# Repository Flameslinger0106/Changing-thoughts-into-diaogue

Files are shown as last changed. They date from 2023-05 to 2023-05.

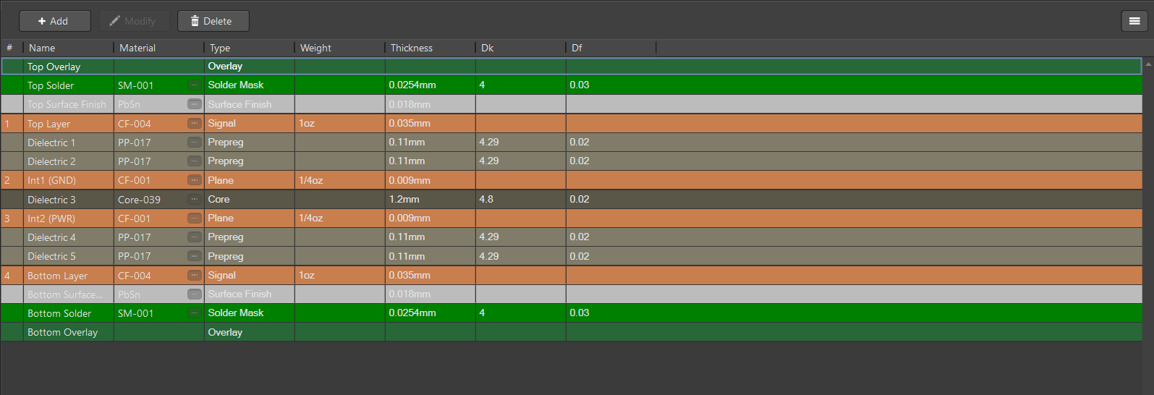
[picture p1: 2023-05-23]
Layer stack manager.PNG

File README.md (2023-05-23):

# Changing-thoughts-into-diaogue
This repository contains the Altium PCB design for a project that we had in which we had to convert thoughts into audible dialogue.

There is a report attached alongside the actual files associated with the design that contains all the restrictions that were to be taken into account while designing the said PCB.

If you are having difficulty in understanding the motive or working please look at the "Report file for T-A project" in the file section.

Please do not copy and paste the files as they are and make sure to email me first at - anmolyadav0106@gmail.com if you need to talk about importing certain parts of the project.

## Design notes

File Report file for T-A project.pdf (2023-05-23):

Mohammed Arib z5208042

Ashish Dutta

Jack Walsh

Anmol Yadav

# ELEC4123 ELECTIVE TASK REPORT

TABLE OF CONTENTS

PROBLEM STATEMENT

The overarching design problem was collectively perceived by the team to be: “Electronically translating a patient’s thoughts into accurate and audible dialogue.”

IMPORTANT FEATURES

- Must think about the practicality of the design approach. Is it viable to use in real life? How is it powered? How does it interact with the patient?
- Interfacing between tasks.

FILTRATION

Upon initial research and inspection of the signals provided, it was discovered that EEG signals occupy microvolt level amplitudes. Also, these signals are highly susceptible to noise (such as muscle movements, eye saccades and pink noise).

Key challenges are:

- To amplify the EEG signals to MCU voltage range with low distortion and noise.
- To find a balance with the trade-off between the noise reduction circuitry and minimising component noise. More components means more noise reduction functionality but more components also means more component noise.

SIGNAL PROCESSING

The goal is to achieve a high detection rate in real time. The best algorithms that give good detection rates have higher time complexities, hence they are harder to implement in real time.

Key challenges are:

- Balance the trade-off between real time processing speed and effective detection rate.
- Navigating ambiguities in breaking down a large signal into smaller words to mimic regular human speech, i.e., what is a reasonable ‘frame’ size?

AUDIO PRODUCTION

Key Challenges are:

- Taking a low voltage analogue signal and amplifying it whilst maintaining a delicate balance between efficiency and THD/spectral characteristics.
- Keeping efficiency high while minimising power consumption which would require a balance between complexity and component count.
- Modelling and accounting for the non-idealities of a realistic speaker.

CONSOLIDATION

It is important to consider how all the tasks will come together to work as one holistic system to ensure outputs remain precise and it is safe to use in a medical environment.

Key Challenges are:

- Condensing all tasks onto a PCB of minimal size so it is practical for real life use
- Minimising signal interference (such as cross talk, ground loops, parasitic capacitance, EMI) for accurate functionality.

BEHAVIOURAL CHALLENGE

- The large breadth of knowledge required to breakdown and complete the task and the difficulty in distributing tasks among the team based on individual expertise and availability

DESIGN CONCEPT AND REASONING

OBJECTIVES & BENCHMARKS-

FILTRATION

The main objective for the filtration part of the circuit is to aim for a balance between noise reduction circuitry and minimizing component noise.

For this part, it is ideal to implement a gain amplifier to make it easier for the microcontroller to sort the input signals into its corresponding bands.

Benchmarks to achieve:

- Realistic noise figure for the filtration part of the circuit is around 2dB-15dB
- ADC selection with high GBP and High slew rate
- Low input referred noise of around 1nV/√Hz
- 3dB cut off at 40Hz for matching the signal bands

SIGNAL PROCESSING

Key objective is to detect the input signals in real time for outputting through a speaker.

Benchmarks to achieve:

- Sampling and Time resolution: Bounded by the Nyquist criterion to avoid aliasing. Sampling rate of at least 256Hz must be chosen.
- Feature extraction scheme: Timing must be real time i.e., processing time on the order of 300ms - comparable to buffer size.
- Detection rate: Must accomplish at least 95% for a usable experience.
- Buffering: Simulate real time audio pause. 300ms pause
- Noise performance: Must still achieve >= 95% detection rate in non-ideal conditions.

AUDIO PRODUCTION

Objective for this part includes creating a Power supply for the first two parts of the circuit as well as making sure the output is relayed through the speaker.

Benchmarks to achieve:

- Bandwidth and flatness: Bandwidth roughly 20k because of limits for human hearing bandwidth 3db drop off should be between low: 20hz, high: 20khz
- Open loop bandwidth: required to be high
- Power delivered: Low as reasonably possible, limit on active biasing etc. Balance with efficiency - 40mW
- THD: the main focus, below 1% and ideally 0.1%. Achieved through a closed loop system that linearizes the output over the crossover distortion period (refer to Deliverable 4)
- AB amplifier choice
- Limit the component count. Zobel network tuning to particular TSP

SOLUTION & REASONING

OVERVIEW OF SOLUTION CONCEPT

Low-noise preamplifier | Microcontroller (feature extraction)

Power amplifier speaker output

FILTRATION

Challenge 1:

To amplify the EEG signals to MCU voltage range with low distortion and noise.

Noise filtration is achieved with a low noise amplifier, low pass filtering and active removal of noise sources. EEG input voltage range is 10-100uV, output range is 0-3.3V.

Key methods to overcome this challenge were:

- Putting op amps in parallel to improve spectral noise characteristics
- Choosing low noise amplifiers
- Performing second order low pass filtering
- Using adjustable gain amplifier to

Meeting objectives:

Through a component choice of low noise precision op amps, an average noise figure of 3.57db was achieved. Furthermore, small resistor values were used to keep component noise low.

Challenge 2:

To find a balance with the trade-off between the noise reduction circuitry and minimizing component noise.

This challenge was met by experimenting with different op amp configurations. Initially only one op amp was used for the preamplification, however, noise at the output was relatively high. Parallelising op amps reduced noise spectral density overall however increased space on the PCB. The optimal number of op amps used to solve this problem were 6. Any less and the output had more noise and any more than 6, and component noise and space increases didn’t justify the use.

To simulate component noise, a variety of noise sources were added simulating the effect of an additional component.

Meeting objectives:

Noise was significantly attenuated using low pass filters hence high frequency noise above 40hz was reduced significantly.

SIGNAL PROCESSING

Challenge 1:

Balance the trade-off between real time processing speed and effective detection rate.

In order to meet this challenge effectively, a hybrid implementation of short-time Fourier transform (high speed, lower complexity, mediocre detection rate) and peak detection for detecting false positives for beta band (higher complexity, slower speed). Hence by utilizing this approach a balance was achieved between approach complexity and computational complexity.

Meeting objectives:

Upon implementation of these methods a detection rate of 96% was recorded across all samples and custom test cases. Furthermore, this approach allowed real time processing.

Challenge 2:

Navigating ambiguities in breaking down a large signal into smaller words to mimic regular human speech, i.e., what is a reasonable ‘frame’ size

For the solution concept to meet this challenge, a literature review was conducted for obtaining lengths of pauses in natural speech. Similarly, the frame size (after research) was chosen to be 1sec to mimic the patterns of user thought. The output between words was buffered using a 0 padded signal with an average buffer size of 0.3seconds, and the processing speed was fast enough to process the next frame whilst buffering was occurring -offering a seamless experience.

Meeting objectives:

Here the frame size, buffer length and sampling rate choices allowed the solution concept to effectively break apart the signal and deliver a user experience worthy of usage.

AUDIO PRODUCTION

Novel features: Adjustable volume control, component minimisation, Zobel network, extremely high bandwidth, outstanding THD, minimizing cross-over distortion

Challenge 1:

Taking a low voltage analogue signal and amplifying it whilst maintaining a delicate balance between efficiency and THD/spectral characteristics.

To meet this challenge a choice was made between class A, B and AB amplifiers. Class A amplifiers have low efficiency and low distortion, AB amplifiers have better efficiency and slightly higher distortion, and class B amplifiers have the highest efficiency and highest distortion.[1] Minimizing THD was the key priority, as THD related to the clarity of produced sounds. Efficiency was the next important metric. To strike a balance between the two, a class AB amplifier configuration was used.

Meeting objectives:

Using this method, a THD of 0.1%, higher efficiency approaching 50% was reported. The solution concept minimized power draw to 40mW by minimizing the number of active components in the design.

Challenge 2:

Modelling and accounting for the non-idealities of a realistic speaker.

The mass of a speaker, inductance, capacitance, force of membrane vibration and other key real-world phenomena require extra attention in order to reproduce a realistic model for audible sound. A Zobel network was implemented to tune these electromechanical parameters also known as Thiele/Small Parameters (TSP).[2] This network serves as a practical method to neutralize instabilities at high frequencies, coil inductance and other realistic non idealities.

Meeting objectives:

The implementation of this section culminated in effective gain and bandwidth (2.51 and 1.061Mhz respectively).

HIGH LEVEL BLOCK DIAGRAM

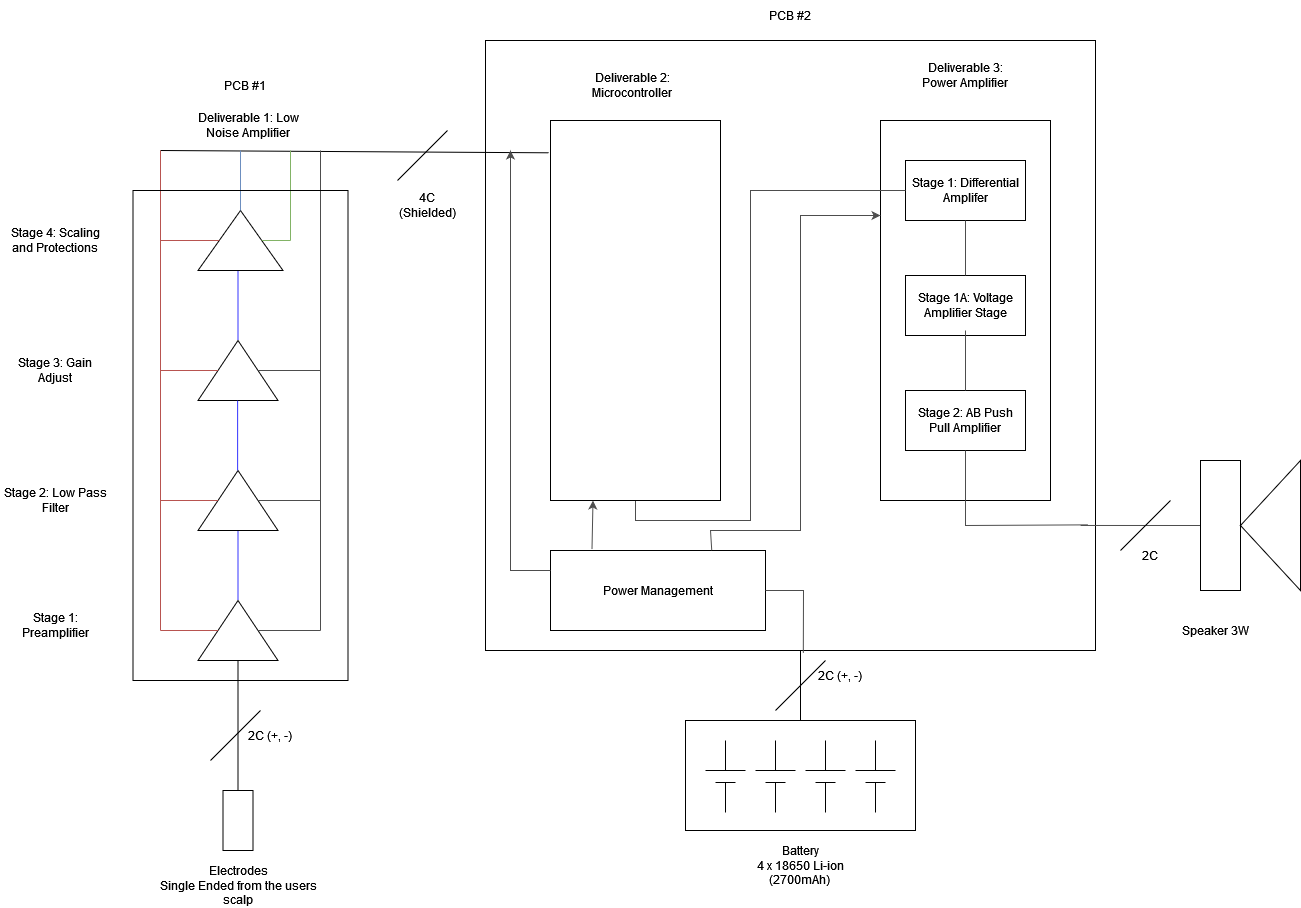
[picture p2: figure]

Figure 1 High level block diagram

TASK ALLOCATION

The tasks were allocated based on each member’s strength and ultimately what they felt the most comfortable with to maximize productivity and reduce any delays caused by lack of fundamental knowledge for their allocated task.

Although each deliverable was primarily handled by one individual, other team members would be often encouraged to pitch in with any suggestions or ideas relevant to the task at hand.

Primarily, task and time allocation for each deliverable and its subcomponent contributors was done through a Gantt chart as shown below. It can be inferred from the Gantt chart how each deliverable was primarily handled individually by each of the group members.

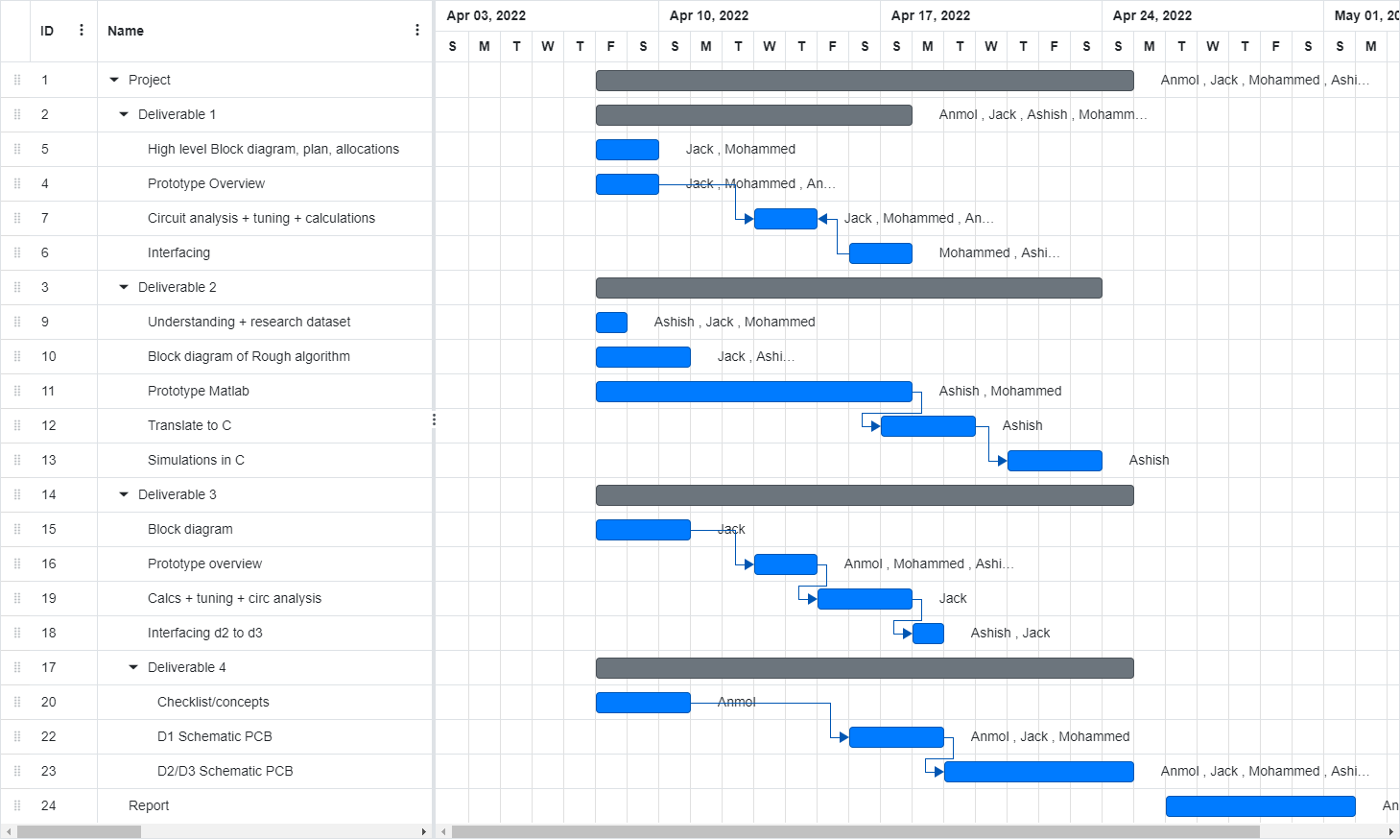
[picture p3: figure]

Figure 2 Gantt Chart

TASK DESCRIPTIONS

DELIVERABLE 1

Author: Mohammed Arib

1.1 INTRODUCTION

EEG signals contain a high amount of random and/or repetitive noise which hinders effective analysis of useful information hidden within the signal. This recording circuit is purposed to extract this information by removing redundant noise artifacts through effective filtration techniques while also amplifying the signal so it can be processed on the MCU.

1.2 NOVEL FEATURES

- Parallel pre-amplifier configuration for better noise performance [3]
- Adjustable gain amplifier to record wider variety of signals such as EMG and LFP
- Removing large noise artefacts such as blinking, unstable electrode contacts, swallowing [4]
- Effective bipolar to unipolar signal conversion to minimise component count
- Minimising PCB size by using an even number of op amps to utilise dual package ICs

1.3 STAGE 1: PRE-AMPLIFIER AND DC BLOCKER

Prior to designing the circuit, it was important to determine whether it is better to amplify before filtering or vice versa. Research shows that filtration should be conducted after low noise amplification to achieve the best possible noise figure [3], this is because filtering attenuates the signal bringing the voltage level close to the noise which would then be amplified giving a poor signal to noise ratio.

The first stage of the circuit is a pre-amplifier which allows the amplification of low voltages with low distortion. This was achieved by using a very low noise amplifier (LT1028) with a voltage noise density of 1nV/√Hz at 100Hz. The total noise density of the amplifier stage was significantly improved by implementing a parallel configuration of pre-amplifiers. For a two-level pre-amplifier configuration, the total input referred noise density is reduced by a factor of √2 [5]. This can be shown for a general number of op amps in parallel with the formula:

Total noise of op-amps = N/√n Where N is the noise density of the op-amp, n is the number of op-amps in parallel

Using the above formula for this circuit, the total input referred noise from the op-amps would be:

1/√2 = 0.7nV/√Hz

The total noise of this stage is further improved by choosing small feedback resistors to keep the impedance level and component voltage noise as low as possible.

The second part of this stage is a DC blocker which is used to remove any offset voltage present in the EEG signal. The blocker uses a simple topology of consisting an inverting op-amp followed by a decoupling capacitor at the output to remove the DC offset. It is necessary to remove any offsets in sounds signals to avoid static and crackling noises [6]. The effectiveness of the blocker can be visualised in Figure 2 and 3 showing the original EEG signal and the signal after offset removal.

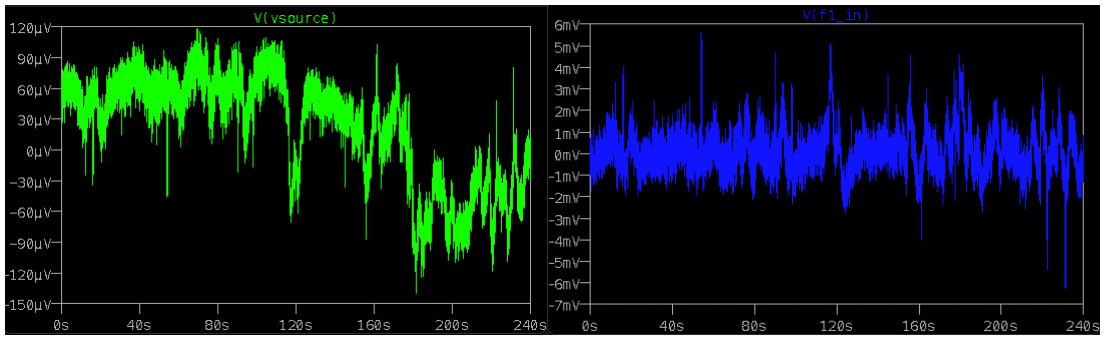
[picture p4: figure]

Figure 3 Original EEG signal with 60uV offset | Figure 4 EEG signal after DC blocker with no offset

1.4 STAGE 2: FILTRATION

The next stage of the circuit is a second order Low pass filter tuned to have a 3dB cut off at 40Hz (shown in Figure 4) to match the range of EEG signal bands from delta to beta. A higher order filter has higher attenuation for frequencies above the bandwidth therefore this stage uses a second order filter for a 40dB/dec drop after 40hz which can be seen in Figure 3.

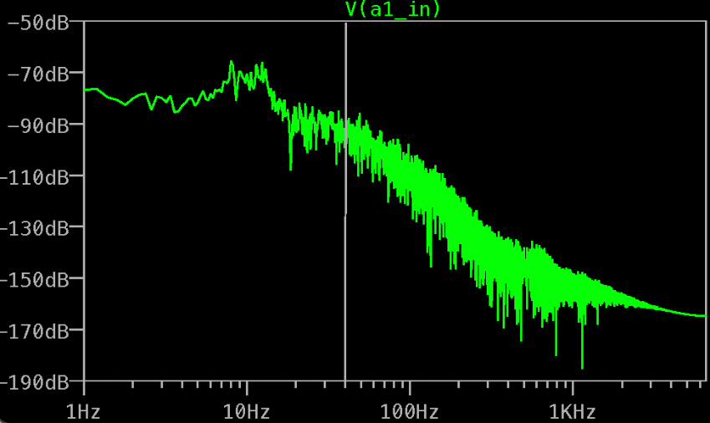
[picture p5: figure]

Figure 5 FFT of EEG signal with 40Hz point marked at grey line

A Sallen Key filter topology is used to construct the low pass filter due to its simple design and the ease of cascading RC components to achieve a higher order filter [7], hence reducing component count. This topology also minimizes the gain-bandwidth requirement of the op-amp so the same op-amp can be used as in the Stage 1 to keep a low voltage density and enable the use of the dual package IC available hence minimizing the PCB area and making the device more practical.

1.5 STAGE 3: ADJUSTABLE GAIN AMPLIFIER

The next stage is used to amplify the EEG signal while maintaining its spectral characteristics to increase the resolution up to the ADC voltage level. This is essential to do so that the signal can be accurately quantised and analysed in the MCU. To achieve this an adjustable gain amplifier is implanted using a simple inverting amplifier with a potentiometer as the feedback resistor.

Literature review states that EMG signals are used to record skeletal muscle activity with an amplitude range of 10-20mV [8] putting them at a much higher voltage level than EEG signals. The potentiometer allows the user to change the feedback resistance, in turn changing the gain of the amplifier to accommodate for signals with a greater voltage level.

Due to the high gain required to bring the signal to ADC voltage level of 3V as shown in Figure 5 and 6, the amplifier, LT1630, was chosen based on its high GBP (30Mhz) and slew rate (30V/us) characteristics. This amplifier also maintains it performance at a low supply of 3V which makes it suitable to use for battery powered systems such as this.

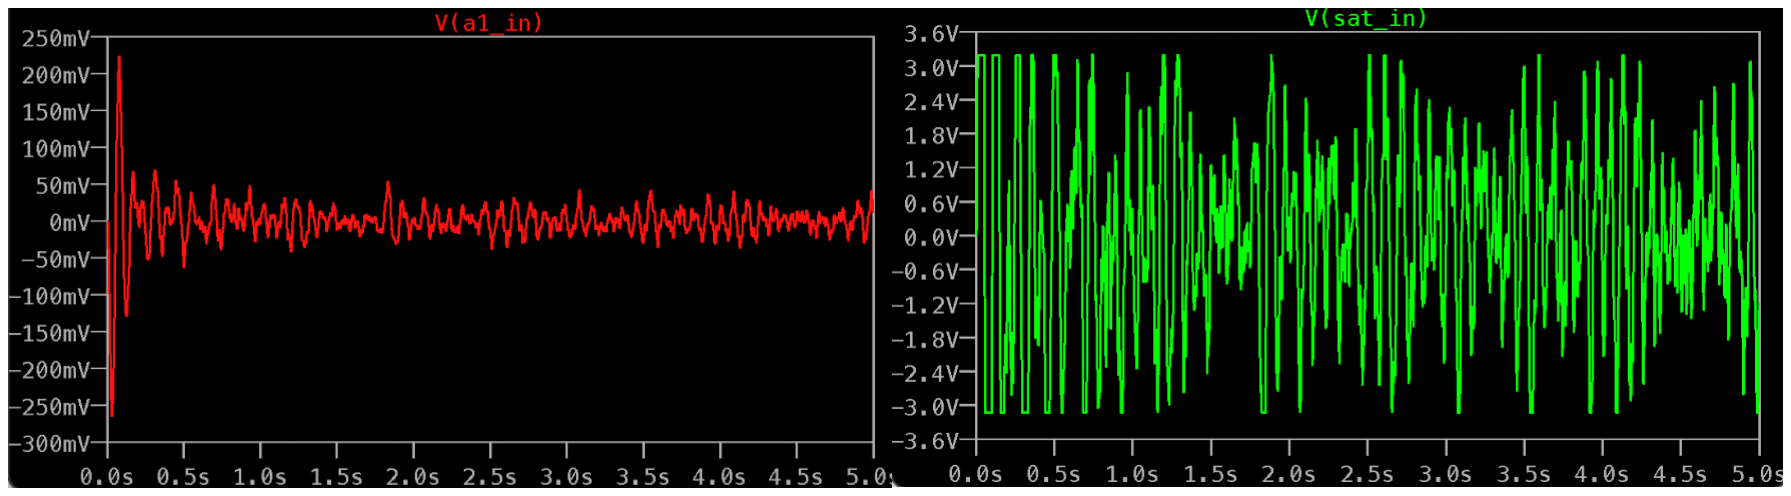
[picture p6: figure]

Figure 6 EEG Signal after LPF | Figure 7 Signal after amplification

1.6 INTERFACING AND ADC SELECTION:

Before explaining the final stage of the circuit, it is important to delve into how this circuit will be interfaced with the MCU and the choices need to be made to achieve that. The analogue signal that this circuits outputs needs to be passed into an ADC before it can be analysed in the MCU. When digitising an analogue signal, parameters such as noise floor and quantisation noise need to be considered.

Noise floor is the sum of the noise each individual component generates in the system [9]. The component noises are accounted for when calculating a noise figure for the system since noise and signal are independently extracted for input and output through LTspice when calculating the noise factor. An ideal noise figure is 0 and through research a realistic noise figure is said to be between 2dB-15dB [10]. The noise figure obtained for this circuit can be seen in the Figure 7 with the peak at approximately 10dB and an average of 3.57dB. Since EEG signals are very susceptible to noise a figure of 3.57dB is acceptable.

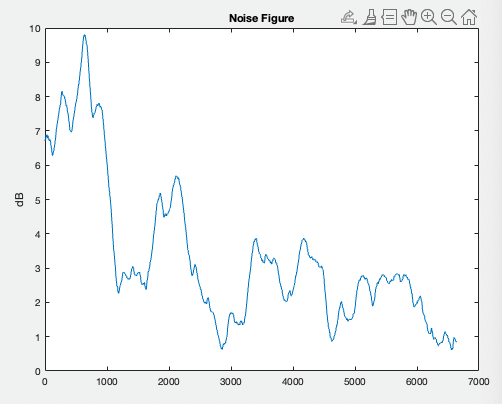
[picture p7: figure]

Figure 8 Noise Figure

Quantisation noise is an inevitable effect of converting an analogue signal to a discrete form. It is caused by rounding errors between the real analogue signal and the bit resolution of the ADC [11]. To reduce the quantisation noise level a low pass filter can be used at the output of the ADC which can be implemented digitally on the MCU.

Taking these parameters into consideration, the ADC built into the MCU will be sufficient for interfacing which would also reduce component count and minimise PCB size. The on-board ADC operates within a voltage range of 0-3.3V and has a sufficient resolution of 12 bits giving a dynamic range of 72.4dB for the system. This will appropriately map the analogue signal into the digital domain.

1.7 STAGE 4: SCALING AND PROTECTION

The final stage of this circuit is a unit gain buffer to convert the bipolar signal to a unipolar signal range which the ADC takes. A comparison between the two signals is shown in Figure 8 below, where the green signal is the output of the adjustable gain amplifier, and the blue signal is the output of the unity buffer.

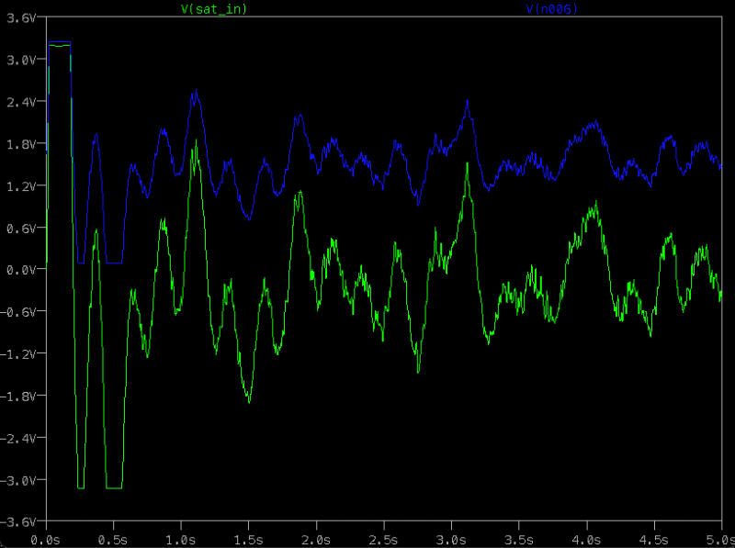
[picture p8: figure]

Figure 9 Output of amplifier vs output of buffer

The op-amp used for this stage does not require any new or unique characteristics compared to the previous stage therefore the same op-amp is used. Also, selecting the same op-amp allows for the use of the dual package IC hence making the device more practical by decreasing the size of the PCB.

The second purpose of this stage is to saturate the signal, so it does not exceed 3.3V to protect the ADC and MCU from overheating.

This is a high priority due to the device functioning in an environment that requires human contact. Frequent saturation of the EEG signals is not ideal since op-amps experience a recovery phase when there is signal saturation and if the signal is large if enough in amplitude, information will be lost in the recovery phase.

Therefore, this buffer protection is acts as the last line of defence and the adjustable gain amplifier must be used to adjust the signal amplitude to avoid saturation for best signal output.

DELIVERABLE 2

Author: Ashish Dutta

2.1 INTRODUCTION

Choose simple, effective, and novel approach. Simple designs mean faster processing times (better for real time analysis) less error prone. Effective designs mean a good detection rate. Novel approach to get new performance and improve probability of patenting- which improves market edge (this task is supposed to mimic a real product after all).

2.2 OVERVIEW

D2 interfacing | Pre-processing data | Process data/feature extraction | Output to
D3.

2.3 NOVEL FEATURES:

- Filter tuning, memory management and computational optimisation
- Peak detection algorithm – weighting EEG bands differently
- High detection rate: 96%
- Ideas from Short Time Fourier transform (STFT)
- Signal denoising, multiresolution analysis
- Buffering output to reflect natural speech patterns

### 2.3.1 Algorithm Breakdown and Parameter Choice:

The discrete input signal is broken down into ‘windows’ or ‘frames.’ Each frame represents a word. A natural question arises, how long should a frame be?

Frame choice was based on the following reasoning:

- If frame length too long: We miss out on information (i.e., words)
- If frame length too short (then we are not representing user’s intentions correctly)
- Correct frame length accurately captures when user thinks of a word.

Based on a paper called “EEG signal processing in brain computer interfaces” by Garces (et al) [13], the rate at which EEG signals fluctuate in conscious Brain Computer Interfaces is roughly 1 second. Thus, the signal is broken down into 1 second windows. Obviously, this criterion does not apply completely to Delta waves which are slow and are usually present in deep sleep or meditation.[14]

From here a short time Fourier transform is performed on the windowed signal. From here the powers in each frequency band are calculated using Parseval’s theorem [15].

### 2.3.2 Parseval’s Theorem:

∑|x[n]|
2

N−1

n=0

=

1
N

∑|X[k]|
2

N−1

k=0

The maximum of these powers is outputted, and the corresponding wav file is outputted. An important issue to note is the uncertainty principle, governed by the equation below.

## ΔtΔf ≥

1
4π

Essentially if there is a good time resolution, there cannot be a very good frequency resolution and vice versa. EEG waves are dynamic in nature and not static. STFT is the best for analysing signals with frequency content that is static, [16] but it does not give the frequency component of a signal at a given time. It only gives the frequency component across a timed window. Although the detection rate was very accurate, future iterations could solve this problem by applying ideas from the Wavelet transform. More depth is given in the reflection section of the report.

In this task only Delta (0-4), Theta (4-8), Alpha (8-12) and Beta waves (12-40hz) were considered, practically speaking, delta waves are dominated by 1/f noise at frequencies ranging from 0-0.5hz.[17]

Hence when filtering the signal, filter cut offs were designed in a way to mitigate large sources of 1/f noise. Although this task does not need to detect gamma waves (40-100hz), noise from surroundings 40-50hz also tends to interfere with signals (especially beta signals at the edge of the 40hz). To reduce this noise, filters with sharp cut offs were chosen.

Novel features of filter choice:

- Optimal window choice (Hamming vs Hanning vs Blackman-Harris)
- Sharp attenuation
- Optimising for filter order to avoid excessive memory drain.

2.4 FILTER CHOICE AND DESIGN THINKING

Initially IIR filters were chosen for their lower computational complexity. Linear phase was not exactly an issue as we only care about the magnitude of the filter response for the calculation of the powers. A Chebyshev filter was chosen as: A small passband ripple distributed across a frequency range does not alter relative powers (as the ripple occurs between all frequency bands) and the Chebyshev filter has a maximal drop off (especially important at the edges of frequency bands to avoid confusion and false positives).

However, upon implementing this in python – the internal libraries did not produce the best filter responses. This is due to the mathematical approximations occurring in python not being able to fully imitate the Chebyshev filter exactly. Hence a quick pivot was done to an FIR approach. A window size of 512 was chosen as:

- Best filter response
- Higher order means more computation and more memory. Higher order approximations did not fare well in terms of this cost benefit.

To further minimise computational complexity, these coefficients were precalculated and stored on the MCU in memory. At run time these coefficients were simply accessed in memory- saving time and speeding up the program.

To further speed up the program even more, powers of 2 were chosen for window lengths; as the internal implementation of many FFT algorithms run faster with vector lengths corresponding to a power of 2.[18]

### 2.4.1 Window Choice:

The windowing function is essential in smoothing discontinuities in the FFT of a truncated signal [19]. The following criteria were prioritised when choosing the filter window:

- Sharp attenuation
- Passband signal preservation (minimal distortion)
- Small sidelobes in stop band

Examined windows: The following windows were available for use in the in-built python libraries.

Hanning:

Main Lobe: Width of the main lobe is comparable to Hamming window however smaller than Blackman Harris (good thing).[20]

Side Lobe: The first side lobe is bigger than hamming, but the distant sidelobes are smaller.

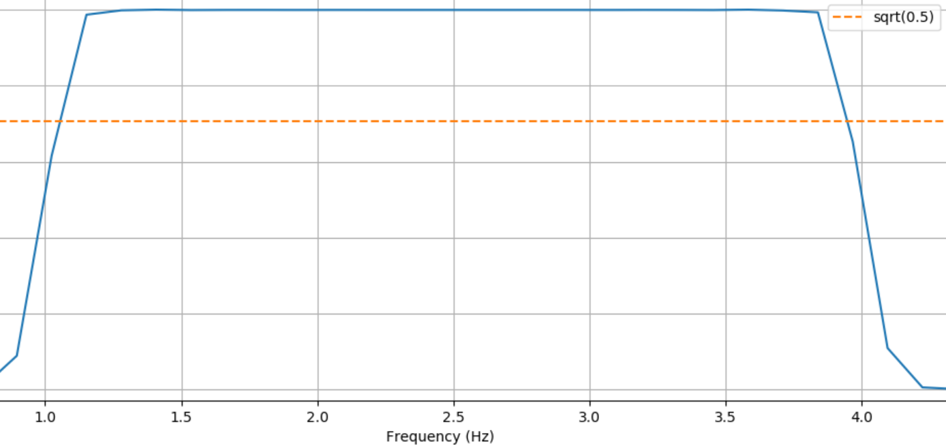
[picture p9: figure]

Figure 10 Hanning Window

Blackman Harris:

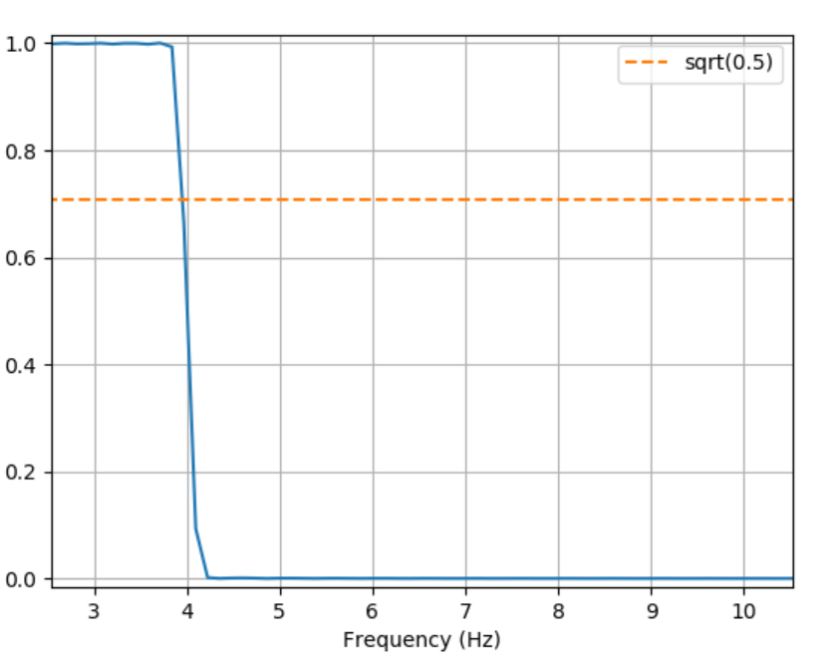
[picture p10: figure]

Figure 11 Blackman Harris Window

Main lobe: is wider than Hamming and Hanning (negative).

Side lobe: drop off sharper than both Hamming and Hanning.[20]

Hamming:

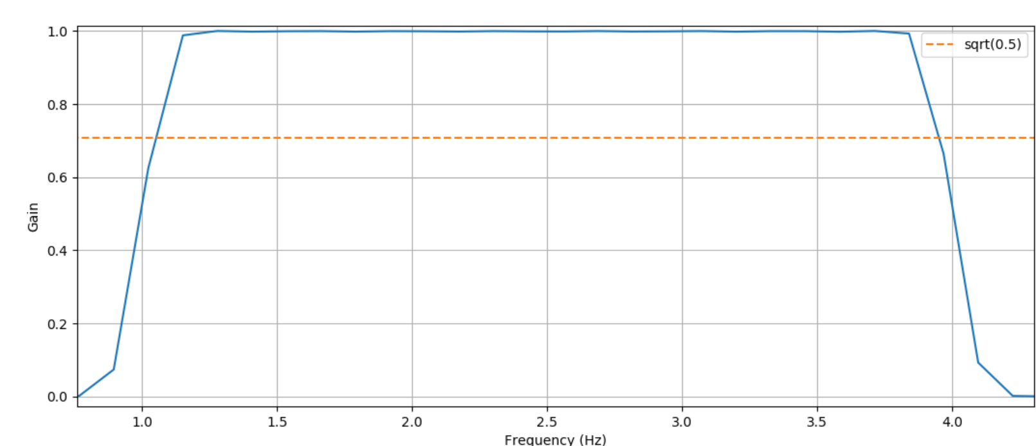
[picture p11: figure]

Figure 12 Hamming Window

Main lobe: width is comparable to Hamming, but smaller than Blackman Harris

Side lobe: First side lobe is considerably smaller (good thing) compared to Blackman Harris and Hanning. However, the more distant side lobes are bigger. [20]

Summary:

Blackman is undesirable as there is less signal (due to the width of the main lobe). With signal powers being extremely small it is extremely important to maximise signal content. Hamming has similar lobe width to Hanning (hence similar signal in the pass band). However, the most important thing is the magnitude of the first side lobe (as the distant sidelobes are not as important). Thus, the Hamming window was chosen.

2.5 PERFORMANCE SUMMARY

A summary of the performance characteristics is given below:

Performance Characteristic | Performance Statistic
Detection rate | 98% (Averaged detection rate across entire signal spectrum)
Timing/Speed of program | Average of 0.3seconds for 5 words
Time resolution | Sampling rate of 512hz translates to a time resolution of 1.953milliseconds
Noise performance | Effective detection rate is still 96% for signals with added pink noise (1/f), white gaussian noise and noise weighted heavily at the edge of each EEG band.

Figure 13 Performance Characteristics

2.6 TESTING:

Testing was first conducted using the sample sets given in MATLAB, both the noisy and clean synthetic sample sets were utilised. Longer form EEG data was passed to the MCU and MATLAB code to determine the behaviour of the program on practical signals.

### 2.6.1 Additional Testing:

Data was carefully generated in delta, theta, alpha and beta wavelengths. This was done by taking the difference of the sample data sets in MATLAB to get the common noise. After this a variety of noise sources were added pink, white gaussian noise, high frequency noise, 40-50hz noise. Furthermore, additional test data sets were generated where the main frequency content resided at the edges of the bands. This was done by taking an FFT in MATLAB for each window of the synthetic dataset and then adding more power to the edge frequencies. After this the Inverse Fourier Transform of the signal was taken to map back into the time domain to give the signal.

The results are summarised in the table below.

Note ‘frequency edge’ data sets still have the noise from the ‘custom noise’ datasets.

EEG Band | Performance
Delta custom noise | 5/5 – 100%
Delta frequency edge | 5/5 – 100%
Theta custom noise | 5/5 – 100%
Theta frequency edge | 5/5 – 100%
Alpha custom noise | 4/5 – 80%
Alpha frequency edge | 4/5 – 80%
Beta custom noise | 5/5 – 100%
Beta frequency edge | 4/5 – 100%
Alpha custom noise (II) Re-run with the peak-detection/normalisation of frequency bands | 5/5 – 100%
Alpha frequency edge (II) | 4/5 – 100%

Figure 14 Additional Testing Results

### 2.6.2 Comments:

Initially, there were higher delta detection rates in the MCU, the reason for this is that the internal implementation in python of the filters were not completely nulling the offset of the DC – resulting in large delta false detections. To counter this the mean of the signal was subtracted in every window. This resulted in smaller false delta detection, completely eliminating the problem, and boosting the performance significantly.

All test results were run through D1 before D2. The output csv/text file was generated from LTSpice. However, having voltages in the output from 0-3.3V did not result in proper wav file conversion. This is because voltage values above a threshold are saturated at 1 in the wav file. Hence for the purposed of interfacing to D2 a voltage division circuit was used to divide values by 3. This was passed to D2, after which all the aforementioned tests were run.

### 2.6.3 Tuning the detection algorithm:

Noise is a random process. Hence, since the Beta band has the highest bandwidth (12-40hz) gaussian noise is more prominently weighted in this band. Thus, the number of ‘false positives’ identifying beta was greater than initially expected. To improve detection rate, the following novel technique was employed:

Peak detection: What distinguished signal from noise in the EEG is conscious thought. Hence a detection mechanism must be employed to give a heuristic prediction of conscious thought (numerically). This peak detection was applied based on realistic values for noise caused by random processes. When the difference between the calculated powers between alpha and beta bands were within the ‘noise threshold’ [21] – peak detection functions were run to distinguish between the 2 bands more accurately.

2.7 TIME, MEMORY & MICROCONTROLLER CODE:

### 2.7.1 Microcontroller choice:

Criteria: Low space, high processing speeds, high memory, on board ADC, DAC of reasonable resolution.

### 2.7.2 Novel choice: Micropython based MCU – esp32. [22]

### 2.7.3 Reasoning:

The specifications were reasonable for the application and the additional benefit of Micropython meant that additional complexity could be added, with little performance trade-off, to improve the detection algorithm. Micropython comes with a highly specialised subset of python optimised for embedded applications and has the added advantage of highly specialised libraries – reducing code complexity.

### 2.7.4 MCU Specifications:

Spec Type | Value | Description/Functionality
ROM | 448KB | Booting + core functions
SRAM | 520KB | Data + instructions
SRAM (Real Time Clock FAST) | 8KB | Data storage. CPU accesses during boot from deep sleep mode.
SRAM (Real Time Clock SLOW) | 8KB | Data storage. Ultra Low Power coprocessor accesses during deep sleep mode.
Clock speed | 8Mhz (Internal) | Synchronise operation of components, instruction execution speed.

Figure 15 MCU Specifications – description taken from datasheet.

### 2.7.5 Memory Calculations:

A key question to be asked is whether the program can both fit and execute on an ESP-32.

### 2.7.6 Calculation Methods:

The length of the program is 306 lines:

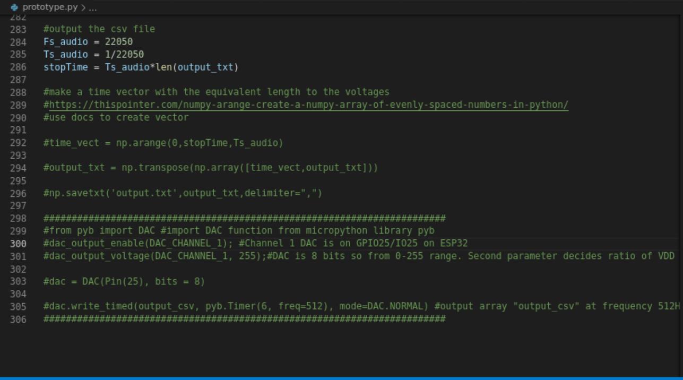
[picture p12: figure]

Figure 16 Length of code

Figure 17 Longest line in code

The length of the longest line is 106 characters. Since a character is stored as 1byte in memory. The size of the total program set is:

106*306 = 32,436B or roughly 32kB << 520kB. Hence the program code fits onto the chip.

The next costly operation is storing the wav files on chip.

The total size of all (uncompressed wav files) is:

Figure 18 Txt files for all bands

Total wav size = 75kB + 120kB + 69kB + 117kB = 381kB

Thus the total size of the data on chip is:

32kB + 381kB = 413kB < 520kB.

### 2.7.7 Memory (Run time execution):

The most memory intensive operations in the program are:

- Storing FIR filter coefficients at run time.
- Generating wav file at run time.

The order of the FIR filter is 512. Each filter coefficient is represented using a numPy double which is 8bytes. Hence the total size of the filter coefficients at run time is: 8bytes * 512 = 4096 Bytes or 4kB <8kB. Hence these values can fit onto fast access RAM.

Note that since we have 4 bands (and hence 4 filters), it may be tempting to say that the total size of memory related to coefficient usage is 4*4kB, however a memory optimisation is applied to avoid this. Each filter is generated once in a local function. Upon exiting the function, the local variable is ‘destroyed’ on the stack hence saving memory.

The next biggest bottleneck/problem is generating the wavfile at run time. Storing wav files on the MCU isn’t the best idea and a future design would offload the storage to some external chip or device. Loading the entire wav file in one go would result in memory overflow. The smallest wavfile has 6000 double values. Hence 6000*8 = 48kB > 8kB. Hence storing the entire wav file exceeds limits for fast access ram. However, by utilising a principle known as chunking, to essentially load only data that is needed, we can avoid this.

### 2.7.8 Timing and bitrate calculations:

Host machine: Dell Inspiron – clock speed: 2.5Ghz.

However, this is obviously not the required speed that we want in terms of the MCU, so in order to mimic a real word value a virtual machine hosted in the cloud was used. This firstly, mimics any latency due to any network calls needed to be made, and secondly an environment that somewhat replicates the environment of the MCU can be set up with relative ease. However not perfect this serves as a good estimate of the timing mechanics.

Now in terms of timing when simulating using the virtual machine this program takes 300ms to execute which is the time spent executing in the kernel. Upon executing multiple commands and taking the average, a value of 300ms was achieved.

Figure 19 Code Run Time

Now this was done using the above python command. Note that this includes all the time taken to open, read, write, files, concatenating the output which is the biggest bottleneck in the program.

To further verify the nature of the program execution, the program was again run on an online simulator shown below:

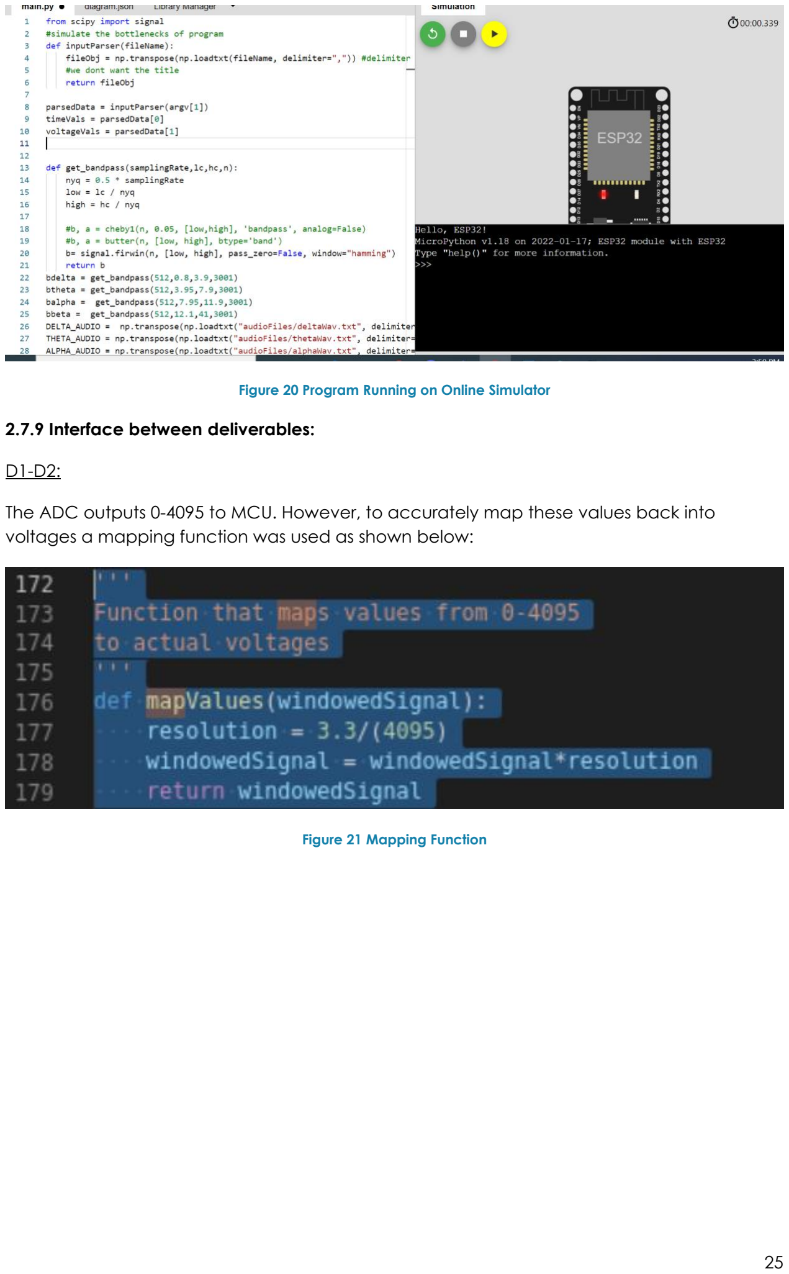
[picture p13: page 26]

Figure 20 Program Running on Online Simulator

### 2.7.9 Interface between deliverables:

D1-D2:

The ADC outputs 0-4095 to MCU. However, to accurately map these values back into voltages a mapping function was used as shown below:

Figure 21 Mapping Function

From here an interrupt routine was setup to sample the ADC pin at 512hz. From here 512 values (window size) are read into a list representing ADV_VALUES. Pin 2 is set for the 12 bit ADC, and upon calling the interrupt handler a flag is set to signal that sampling is occuring.

Figure 22 Interrupt Handler

D2 – D3:

Upon identifying the most prominent band (delta, theta, alpha, beta etc) a wav file is to be outputted to D3. This is done via an 8bit DAC. The required output wav file is retrieved in chunks and is concatenated to a final output file. In between every word there is a small buffer added to make the words identifiable.

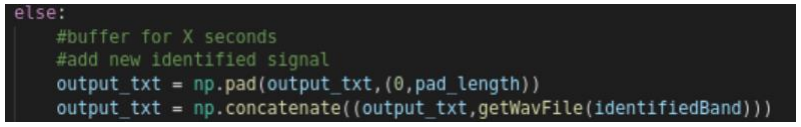
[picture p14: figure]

Figure 23 Addition of Buffer

The size of this buffer is chosen via the subsequent research. According to Jordi Adell (et al.) “Structure of pauses in speech and the classification of speech type,” there are multiple pause types between words “acoustic (silent, breath and filled) and syntactic.[23] To simulate realistic pauses, a paper that examined the average differential of pauses between a large data set of human speakers found that 0.3 seconds was a best guess heuristic.[24] Hence, utilising the sampling rate of the output signal, the length of a 0 padded buffer was calculated to give realistic pauses between words.

DELIVERABLE 3

Author: Jack Walsh

3.1 INTRODUCTION

Deliverable 3 required designing a circuit that can amplify small signals to deliver high power to low impedance circuits. The topology of the solution follows a three stage H.C. Lin Amplifier [25].

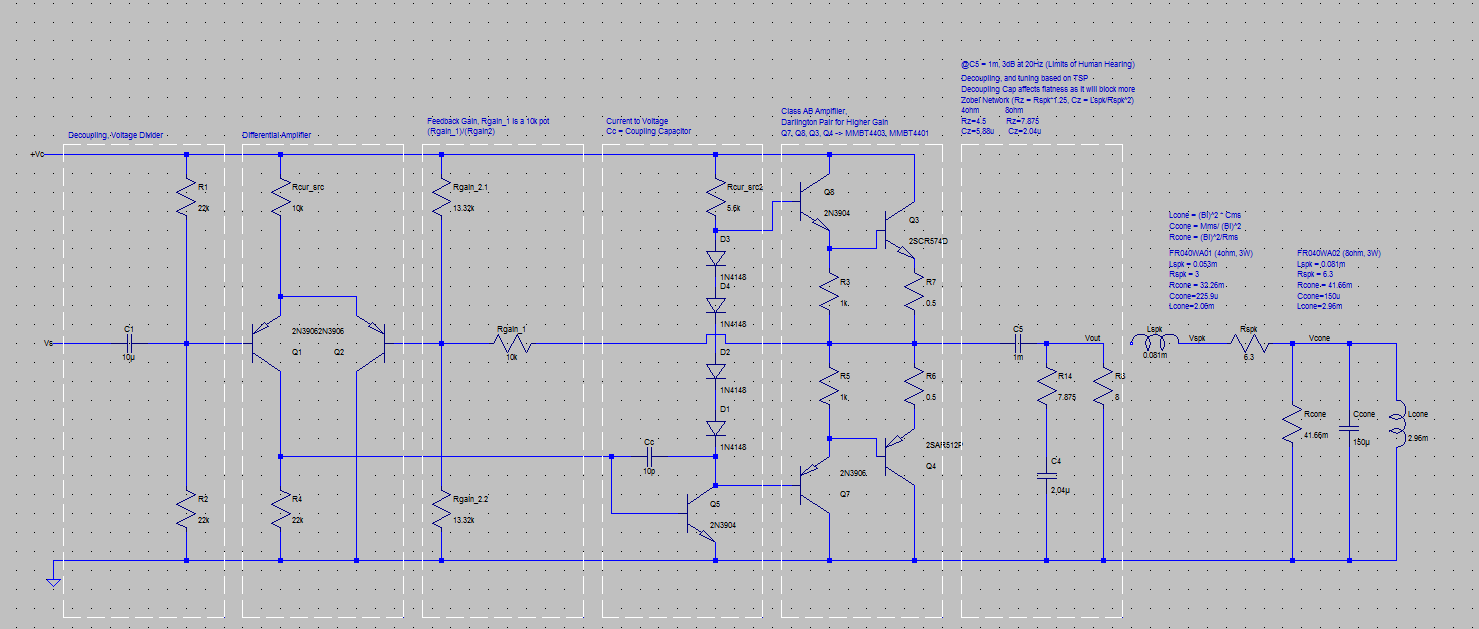
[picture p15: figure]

Figure 24 Completed Design in SPICE

3.2 SYSTEM ARCHITECTURE

### 3.2.1 Input Stage

From Deliverable 2, a signal between [0, +3.3V] is input to the Deliverable 3. This signal is decoupled and offset to the amplifier power supply. This offset is used to ensure that all voltages will have a positive associated current to deliver to the differential amplifier. The differential amplifier acts as high impedance load to DAC while also creating a linear output to the next stage. This property is achieved from comparing the input and output of the entire amplifier as demonstrated in the figure below.

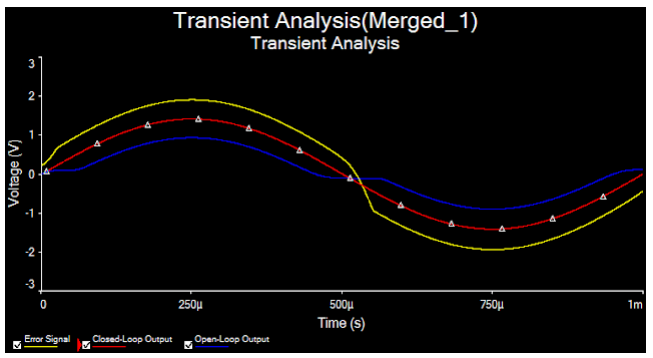
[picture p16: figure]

Figure 25 The differential amplifier linearising the output [26]

### 3.2.2 Voltage Amplifier Stage

The output from the input stage feeds into a BJT with a small compensation capacitor to improve smoothing and create a high frequency pole. This configuration is used to convert the current to a voltage with a gain of set by the beta of the transistor with the fixed current source.

### 3.2.3 Output Stage

This system takes the output from the voltage amplifier and amplifies the power and current by using a Darlington pair of bipolar transistors. The max power is limited to the supply voltage and the speaker resistance. The push-pull Darlington amplifiers are used to eliminate crossover distortion of a class B and the diodes are implemented to improve the efficiency as the transistors are biased.

### 3.2.4 Additional Features

The output stage feeds a Zobel Network before outputting to the speaker. The output is also routed back to the differential amplifier to provide negative feedback and create an error signal that will help to linearise the output. The speaker was determined to be an 8Ω 3W speaker as described in the Speaker Choice Section. The Zobel Network is tuned to the TSP data of the specific speaker that was selected, through the following formulas:

Rz = Rspk

2

Cz =

Lspk
R2

2

Adjustable Gain for volume was integrated into the feedback circuit. This allows the consumer to adjust the volume to different dB levels.

3.3 SYSTEM INPUT AND OUTPUT PROOFS

Figure 3 shows the input and output power relative to the signal power to show the amplification to a resistive load

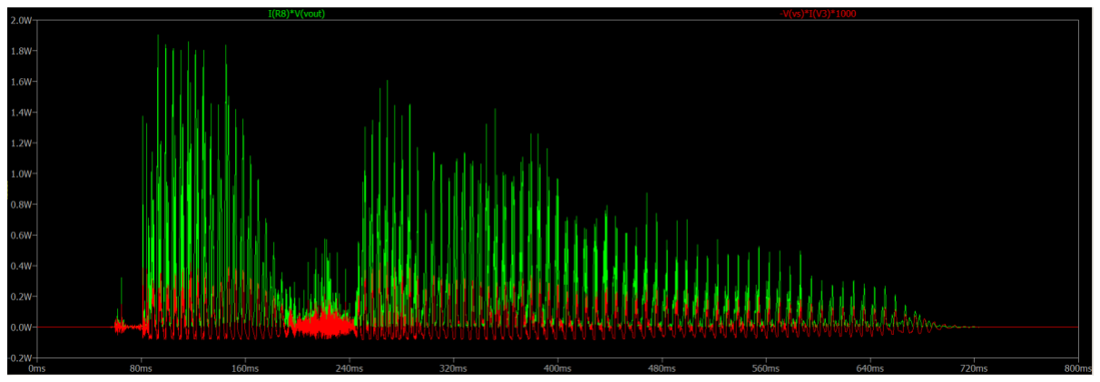
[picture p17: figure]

Figure 26 Simple Modelled Speaker Load Response, Input x1000

Figure 4 shows the input and output power relative to the signal power to show the amplification on a “realistic” model. This model accounts for the real-world characteristics such as the moving mass (Mms), mechanical resistance (Rms), suspension compliance (Cms) and force factor (Bl) using the following formulas to translate into electrical components.

Lcone = Bl

2
∗ Cms

Ccone =

Mms
Bl

2

Rcone =

Bl²

Rms

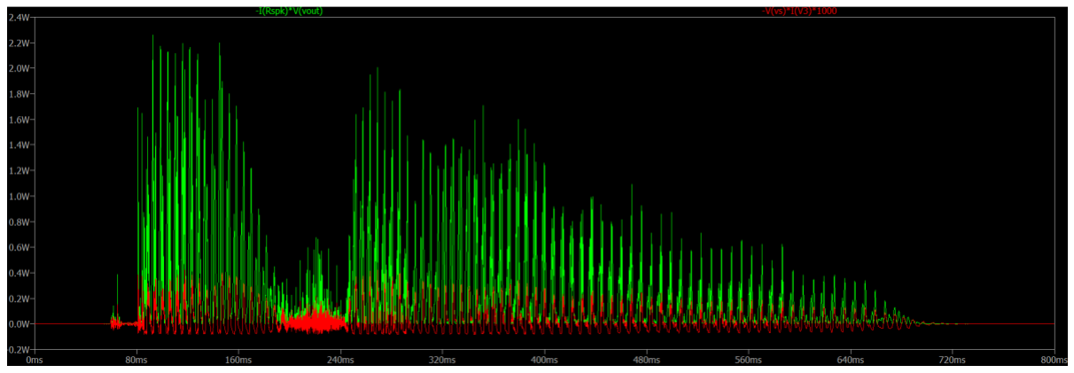
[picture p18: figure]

Figure 27 Realistic Modelled Speaker Load Response, Input x1000

3.4 GAIN AND BANDWIDTH

The bandwidth upper limit is dominated by the miller capacitance in the VAS. This is given by the formula

fupper

= 1/(2π1.5Cc

) = 1.061MHz

flower = 25Hz

This means that the amplifier should have a 3dB drop off at these two bands. In the realistic model, the upper bound pole is closer to 11kHz as seen in Figure 5. This is due to the realistic model of the speaker which has a high pole corner frequency, which can be seen in the SPL Response in Figure 10.

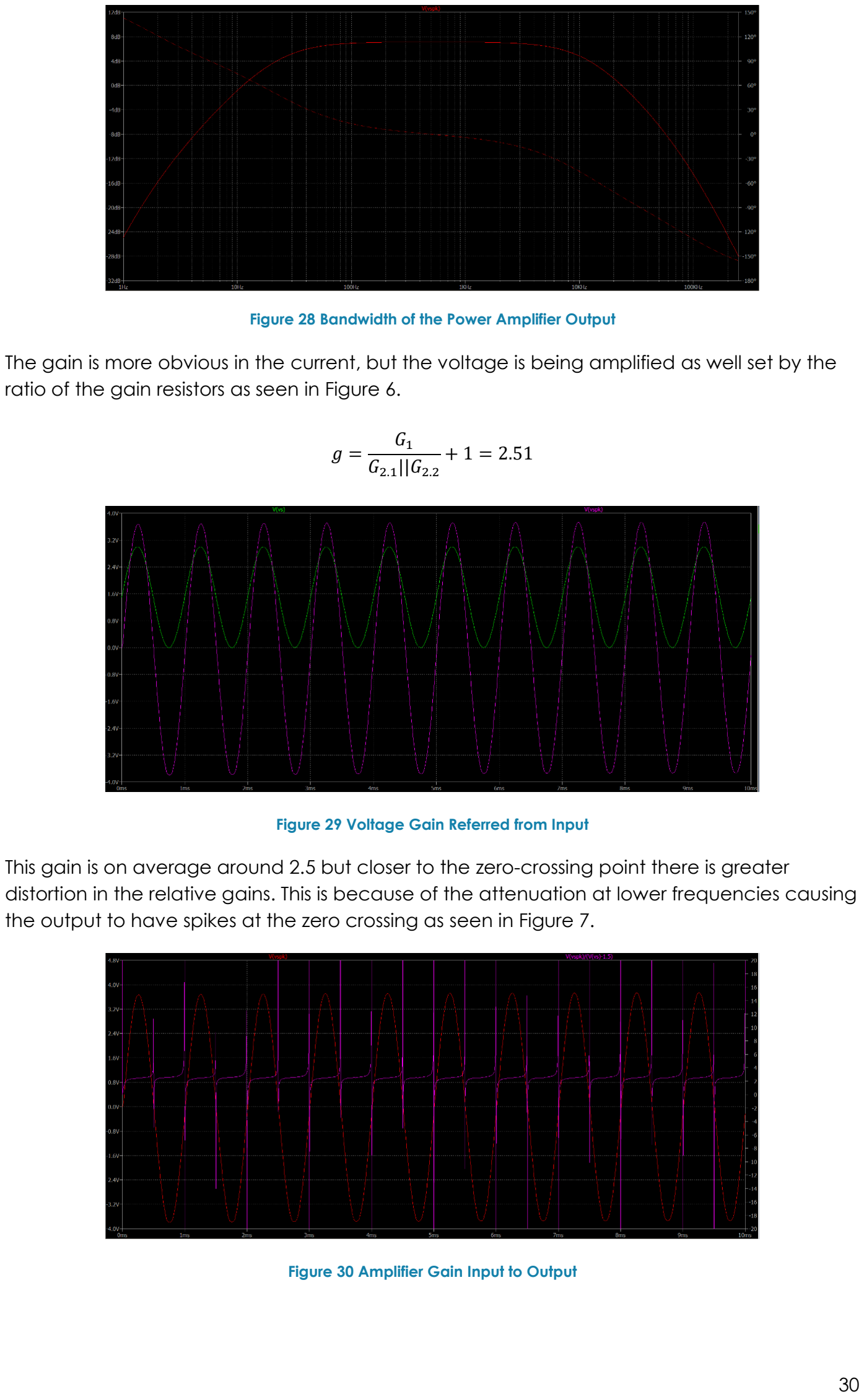
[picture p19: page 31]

Figure 28 Bandwidth of the Power Amplifier Output

The gain is more obvious in the current, but the voltage is being amplified as well set by the ratio of the gain resistors as seen in Figure 6.

g =

G1

G2.1

||G2.2

+ 1 = 2.51

Figure 29 Voltage Gain Referred from Input

This gain is on average around 2.5 but closer to the zero-crossing point there is greater distortion in the relative gains. This is because of the attenuation at lower frequencies causing the output to have spikes at the zero crossing as seen in Figure 7.

Figure 30 Amplifier Gain Input to Output

3.5 OUTPUT POWER

The output power is limited to the transistor selection on the output stage. The 2SCR574D and the 2SAR512P were selected such that the power is always less than its maximum rating. Since the largest PNP transistor can dissipate 2W, the maximum output power was fixed at 2.2W. The output power can be adjusted through a potentiometer on the gain between 0 -10k (Gain would be 0 to 2.5).

3.6 TOTAL HARMONIC DISTORTION AND LINEARITY

The Total Harmonic Distortion has been calculated for 3 different signal types (square, triangle, square) at 3 different frequencies (100Hz, 1kHz, 10kHz). The table below summarises the information

Hz | Sine | Triangle | Square
Expected | 0% | 12.4% | 42%
0.1k | 0.2% | 12.44% | 43.2%
1k | 0.3% | 11.50% | 39.82%
10k | 0.2% | 5.29% | 19.1%

It should be noted that square waves have poor THD due to the decoupling that occurs at the input and output stages. The DC can’t be passed so it slowly dissipates and causes poor THD. Additionally, the filtering that occurs at the compensation capacitor can cause high frequency signals such as the 10kHz, triangular wave can distort to look more sinusoidal on the output.

Linearity can be discussed in the Gain and Bandwidth Section as the linearity relates to gain. Refer to Figure 7 for the Linearity and Refer to Figure 5 for the Flatness.

3.7 EFFICIENCY

Efficiency of a Class AB Amplifier can range between 50-75%, however there is some power consumed in the other two stages. To calculate the average efficiency over a signal, the output from D2 that is correctly scaled by the DAC is fed into the LTSpice simulation. After the sample has run, the RMS Value over the duration of the signal can be displayed (Figure 8). The efficiency can be calculated as follows:

η =

Pin

Pout

=

186.59mW
717.32mW = 26.01%

Additionally at a single tone frequency (1kHz) The efficiency is around 52%. The efficiency goes down as the voltage input is reduced, as the overhead power drain is till there, so for lower voltages the system is less efficient.

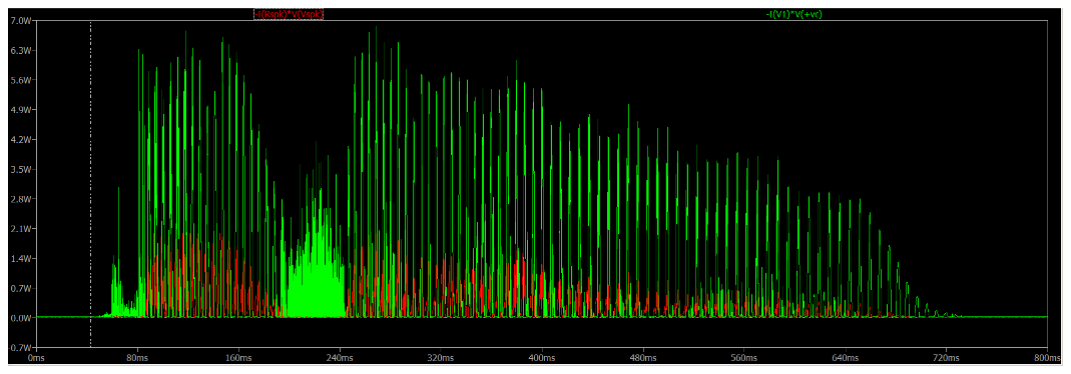
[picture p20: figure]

Figure 31 Amplifier Efficiency from Deliverable 2

Power is lost in the main output transistors which are only allowed to dissipate a maximum of 2A at a maximum power rating of 2W for the PNP transistor and 50W for the NPN transistor. The RMS power dissipation is 252.44mW (NPN) and 237.5mW (PNP). The quiescent current draw is 36.18mW due to biasing All other power consumption over the audio is equal to:

Potℎ = Pin − (Pout +PPNP + PNPN) = 40.79mW

The crossover distortion is 8.3us on the rising edge, and 3.6us on the falling edge of Q4. Over a 0.5ms period the total cross over distortion is 2.38% of the time that both BJT’s are on. This is what creates distortion at the output and can cause the current through the circuit to momentarily spike.

3.8 SPEAKER CHOICE AND MODEL

The Speaker Choice was determined on the maximum current could be provided without compromising on THD with limited voltage. In addition, some research was conducted on the power required to replicate the human voice which was on average 70dB [27]. An 8Ω, 3W speaker (FR040WA02) has an SPL Profile (Figure 10) that is around 85dB at 1m away driven by 1W. Since our maximum output is 2.2W and this value is already over the average human voice, this speaker fulfilled the conditions needed to use in our design.

Since there was an 8Ω and a 4Ω version, the 8Ω was selected so that the amplifier could have increased power with lower current, since this was a limiting factor in both efficiency and heat dissipation in the power amplifier.

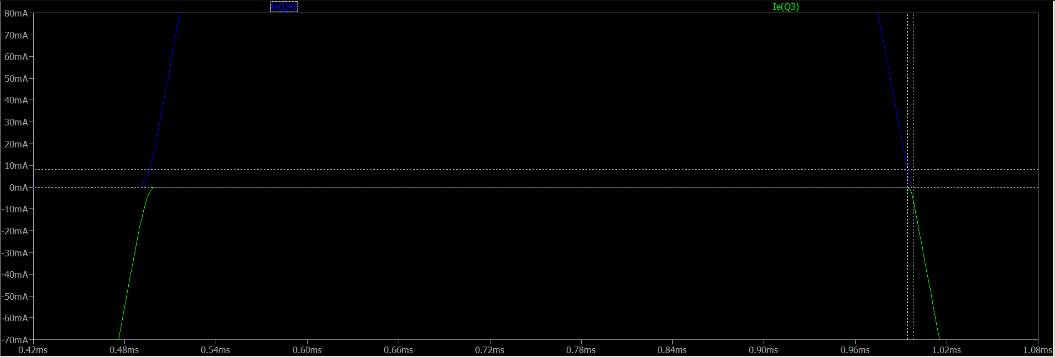
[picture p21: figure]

Figure 32 Transistor Switching at the same time

Figure 33 Speaker SPL Response [28]

DELIVERABLE 4

Author: Anmol Yadav

4.1 INTRODUCTION

Creating the PCB is the culmination of all other deliverables in a presentable format that has been thoroughly tested through design rule checks for validity of the PCB design.

4.2 DESIGN DECISIONS

Since the PCB for D1 is separate from the PCB for D2 & D3, they both had to be created on a separate PCB workspace with their own different Stackup and rules.

We had created a set of baseline rules that had to be followed as either of the PCB’s design case restrictions along with the restrictions in size of the PCB as mentioned in the task worksheet.

Every capacitor and resistor were chosen based on their tolerance values and their minimum power dissipation while also keeping an eye on the cost side of things.

4.3 NOVEL IDEAS

- Decided to place components on the bottom layer of the PCB 1 to meet the size requirement
- Thought about how to implement shielding (Can’t implement in Altium) in an actual real-life setting [29]
- Since we had low frequency our Return Current Path in ground flowed directly from load to source. [30]
- Opted for SOIC type components instead of Through Holes
- Minimalistic Header pins for cost effectiveness
- The BOM total revealed the cost for the components to be $58.645. Best Quality while keeping cost in mind.
- Signal tracks were small (Power tracks take up most of the length!)

4.4 TRACE WIDTH AND VIAS

To determine the trace width and whether it was feasible we used a program called Saturn and input our other parameters which gave us a workable value of around 0.3mW as our allowable power for the circuit for D1 (which is plenty!).

The minimum track width was 0.1mm, preferred track width was 0.15mm and maximum track width was 0.2mm. [31]

This not only enabled us to drastically reduce the size of our PCB but enabled for some easy routing and flexible via placement.

We had 31 vias, most of which were connecting resistors and op amps connecting to ground and power plane since our PCB has 2 layers dedicated for a Power and a Ground plane.

21 of these vias were for signal bus and the other 10 were for getting the power/connecting to the ground plane.

Via diameter is 0.7mm and the signal vias are ‘through’ vias which go from the top to the bottom layer.

4.5 DELIVERABLE 1 PCB

Since D1 had a lot of op amps and a small workable space area (restrictions!), we opted for a 4-layer PCB design choice as that enabled us to free up some space and barely squeeze in all our components into the PCB.

We changed the design from 4 decoupling capacitors to a single capacitor of equivalent value because of size constraints in the PCB.

Since the frequency of the signals that we were dealing with were small, we went for higher dielectric values for our layers.

### 4.5.1 Layer stackup for PCB 1

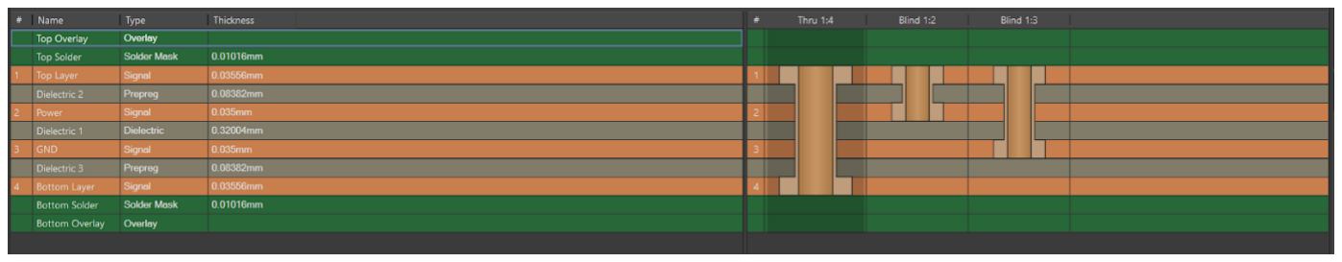
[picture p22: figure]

Figure 34 PCB 1 Layer Stackup

### 4.5.2 Important parameters for D1 PCB

- Longest Track length is 50.32mm.
- Average Track Length is 24.2mm.
- Board Size is 441.66 sq.mm.
- 4 Layers which are namely Top, Power, Ground and Bottom
- Max number of vias on the signal net are 2

4.6 DELIVERABLE 2 & 3 PCB

Since we had a relaxed space for the PCB dimensions there was no point in opting for more than 2 layers for the PCB 2.

Since this PCB had, more power being transmitted to its components, the track width was widened to 0.254mm which was acceptable after calculating the values from the PCB toolkit.

Everything else including the vias remained the same except that we only had vias going from the top to bottom layer

The terminal block (Jout1) in the PCB connects the circuit to the loudspeaker as mentioned in D3 which outputs the audio.

### 4.6.1 Layer Stackup for PCB 2

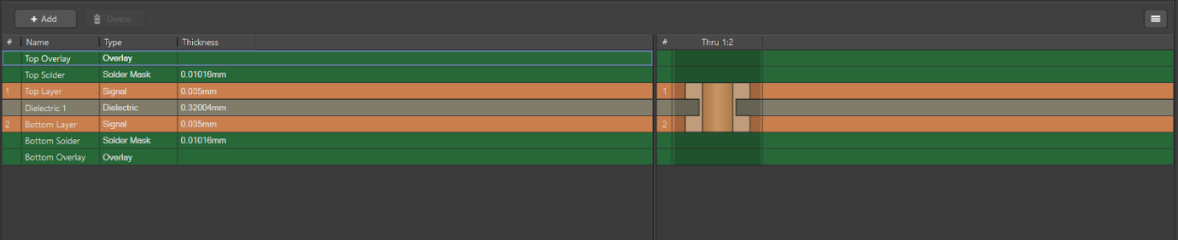
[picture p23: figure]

Figure 35 PCB 2 Layer Stackup

### 4.6.2 Important parameters for PCB 2

- Longest track length is 99.6mm.
- Average Track Length is 51.41mm.
- Board size is 2510.124 sq.mm.
- 2 Layers namely Top and Bottom.
- Max number of vias on the signal net are 2

REFLECTION

THE PLAN

Any project or design that has to be worked upon as a team needs to have proper allocation of tasks for each of its members and a strict timeline.

Our group’s plan of action was to first create a Gantt chart to set a basic timeline structure for everyone to work on. This enabled all the team members to be organized and work efficiently.

We distributed the tasks according to every member's strength and the areas that they were comfortable in.

What we hoped to achieve was to get working on D1 as soon as possible and then move onto the other deliverables after some progress and looking back at it now, it turned out well as we had plenty of time to perform tests and improve upon our ideas for almost every deliverable.

During the long weekends we faced certain difficulties in coordination of the meetings, but we managed to work on individual assigned tasks.

In order to maximize the meetings time with our mentor, Yeoh, we pre formulated questions for each deliverable and the issues that we were facing to get some insight into solving those problems which helped us to minimize idle time during meetings and keep them short and concise.

Since discord has a very good and clean format for working as a team on a task, we opted to create a server in which we collaboratively worked upon. If there were any problems with any deliverable, whoever was available at that point of time would hop on and try to solve the problem. This helped build a sense of bonding within the team and encouraged conversations.

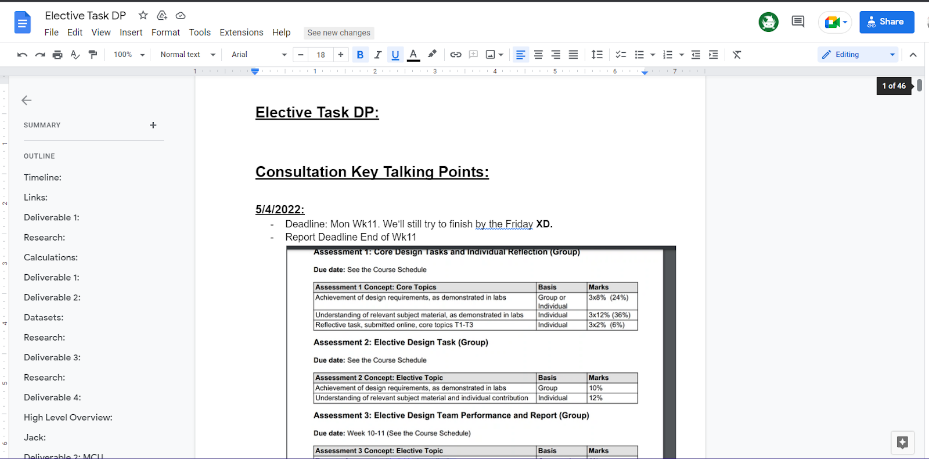
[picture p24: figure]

Figure 36 Common Elective Document

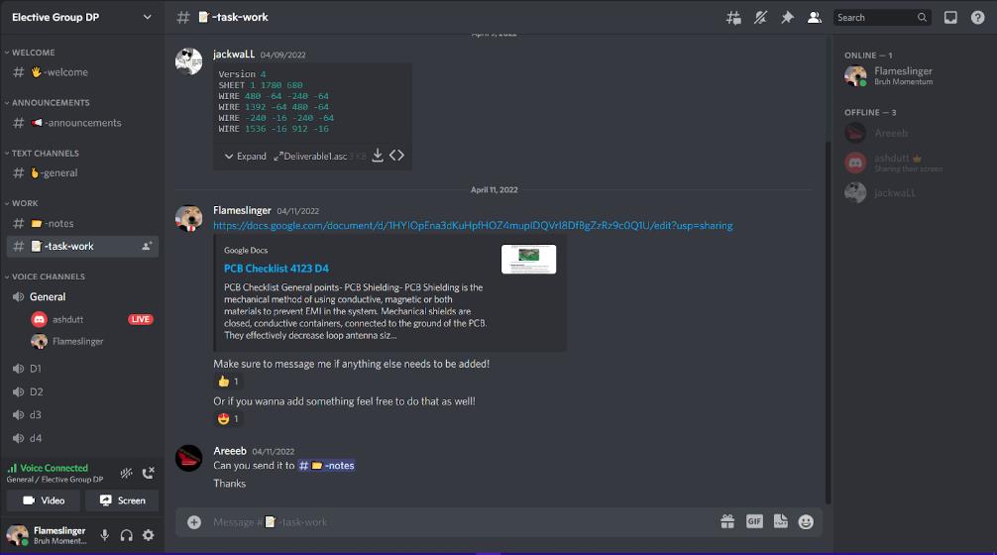
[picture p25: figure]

Figure 37 Discord Server

DELIVERABLE SPECIFIC IMPROVEMETNS

Deliverable 1: Some minor improvements for D1 would be:

Tune the low pass filter for a better bandwidth for the higher frequency signal such as Gamma band (40-100Hz) & LFP (100-500Hz).

Deliverable 2:

- Interfacing a 16MB external chip to improve the storage of audio files.
- Implementing a wavelet decomposition allows us to better understand the transient nature of EEG signals. The wavelet transform serves as a generalised Fourier transform that gives the frequency content of a signal at various regions of time by applying a scaling function on a ‘wavelet’ function – which acts like a windowing function. This is in stark contrast to something like the Short Time Fourier Transform which has a ‘fixed’ window. By varying window behaviour, the fundamental essence of an EEG signal can better be captured in the mathematics leading to practical detection. [32]

### Continuous time wavelet transform:

## F(τ, s) =

1 | +∞ | t − τ | ) d
√|s|

## ∫ f(t)ψ

∗ (
s
−∞

t

Where, | ψ=continuous function called mother wavelet

### Discrete Time wavelet transform:

## D[a, b] =

1 ∑ | f[tm]ψ[
tm | − a
b

]

p−1
m=0
√b
Where, | a= τ
| b=s
- Discrete wavelett transform. More efficient for dyadic upper and lower bounds.
- De-noising ECG and MCG signals. [33]

Deliverable 3: For deliverable 3 we didn’t have many issues for the most part.

- That being said, we would definitely want to improve on certain aspects of D3 namely the efficiency, better protection and better current biasing.
- We were happy with the efficiency of our overall design but to one up ourselves we would choose better components for the design with a lower ON resistance to improve the efficiency which would also make the THD look better.
- Another thing we wanted to implement would be to add a better protection for our circuit design. Currently we had multiple linear regulators in our design instead of a PMIC which we would have implemented given that we had a bit more time to thoroughly research and choose the best one for the task.
- Active protection is also an integral part of the circuit, and we could improve it by adding an eFuse instead of the traditional fuse that we used in our PCB in D3. Since not only is the eFuse smaller in size but there would be no need to replace the fuse every time in case of a power surge. Also, the user can set a custom value for the eFuse using external resistors.

Deliverable 4: We faced certain challenges such as limited PCB dimensions and the layer stackup for D1 PCB.

- To overcome the limited space for D1 we opted to put the resistors on the bottom of the PCB to incorporate all the components on the PCB. Doing this also enabled us to reduce the op amp trace lengths which in turn would help us reduce the excess noise that would usually develop in longer trace length with a low frequency signal at the input side of the design.
- Since we had to put in a lot of op amps for D1, we opted for a 4-layer PCB to reduce the number of signal vias and to also prevent huge track lengths for individually connecting everything to a common power source.
- However, there was one fatal error/oversight in the design for D1 PCB and that was forgetting to do a polygon pour for the power plane which kind of invalidated the point of having a separate layer for the power plane. To improve on this, we would definitely do a polygon pour on the PCB to minimize power trace lengths and in turn it would make the PCB less complicated as well as more resistant to white noise from EMI or crosstalk.
- One more thing that we would do to improve is to research & implement on the best materials for the components that can be used in our design, for example- we would opt for ceramic capacitors for their paraelectric nature and also being cost effective or using metal film resistors for their lower noise, tighter tolerances and better temperature coefficients.

REFERENCES

[1] www.electronicdesign.com. (n.d.). StackPath. [online] Available at: https://www.electronicdesign.com/technologies/analog/article/21801654/understanding-amplifier-operating-classeh [Accessed 24 May 2022].
[2] www.wavecor.com. (n.d.). Zobel networks. [online] Available at: https://www.wavecor.com/html/zobel_networks.html.
[3] G, M. and K, S. (2016). [online] Available at: https://www.researchgate.net/publication/306072174_Significance_of_a_Low_Noise_Preamplifier_and_Filter_Stage_for_Under_Water_Imaging_Applications [Accessed 16 Apr. 2022].
[4] Repovš, G. (2010). Repovš G: Dealing with Noise in EEG Recording and Data Analysis 18

Dealing with Noise in EEG Recording and Data Analysis Spoprijemanje s šumom pri zajemanju

in analizi EEG signala. Informatica Medica Slovenica, [online] 15(1), pp.18–25. Available at:

https://ims.mf.uni-lj.si/ims_archive/15-01/15b-21.pdf.

[5] Forum for Electronics. (n.d.). Filter before amplification or amplify before filtering. [online]

Available at: https://www.edaboard.com/threads/filter-before-amplification-or-amplify-

before-filtering.112388/ [Accessed 18 April 2022].

[6] www.analog.com. (n.d.). Paralleling Amplifiers Improves Signal-to-Noise Performance |

Analog Devices. [online] Available at: https://www.analog.com/en/technical-

articles/paralleling-amplifiers-improves-signal-to-noise-performance.html [Accessed 18 April

2022].

[7] Cristina Bachmann, H.B. and Schütte, B. (n.d.). Remove DC Offset. [online] steinberg.help.

Available at:

https://steinberg.help/cubase_pro_artist/v9/en/cubase_nuendo/topics/audio_processing_a

nd_functions/audio_processing_remove_dc_offset_c.html [Accessed 19 April 2022].

[8] resources.system-analysis.cadence.com. (n.d.). Sallen-Key Low Pass Filters: Second-Order

Active Filters with Voltage Amplification and Gain Control. [online] Available at:

https://resources.system-analysis.cadence.com/blog/msa2020-sallen-key-low-pass-filters-

second-order-active-filters-with-voltage-amplification-and-gain-control. (https://resources.system-analysis.cadence.com/blog/msa2020-sallen-key-low-pass-filters-second-order-active-filters-with-voltage-amplification-and-gain-control)

[9] Reaz, M.B.I., Hussain, M.S. and Mohd-Yasin, F. (2006). Techniques of EMG signal analysis:

detection, processing, classification and applications. Biological Procedures Online, [online]

8(1), pp.11–35. Available at: https://www.ncbi.nlm.nih.gov/pmc/articles/PMC1455479/.

[10] McAllister, M. (2021). What Is ‘Noise Floor’ & How Does It Affect Your Music? [online]

Produce Like A Pro. Available at: https://producelikeapro.com/blog/noise-floor/ [Accessed

20 April 2022].

[11] EETimes (2006). EETimes - Understanding noise figures in radio receivers -. [online] EETimes.

Available at: https://www.eetimes.com/understanding-noise-figures-in-radio-receivers/.

[12] inSync. (2008). Quantization Noise. [online] Available at:

https://www.sweetwater.com/insync/quantization-noise/.

[13] Garcés, M.A. and Orosco, L.L. (2008). Chapter 5 - EEG signal processing in brain–

computer interface. [online] ScienceDirect. Available at:

https://www.sciencedirect.com/science/article/pii/B9780128128923000054#:~:text=A%20brai

n%E2%80%93computer%20interface%20(BCI [Accessed 19 April 2022].

[14] Ryan, T. (2021). Binaural Beats for Sleep. [online] Sleep Foundation. Available at: https://www.sleepfoundation.org/noise-and-sleep/binaural-beats.
[15] Wikipedia Contributors (2022). Parseval’s theorem. [online] Wikipedia. Available at:

https://en.wikipedia.org/wiki/Parseval%27s_theorem [Accessed 20 April 2022].

[16] Basso, C. (1997). Spice predicts differential conducted EMI from switching power

supplies. [online] EDN. Available at: https://www.edn.com/edn-access-02-03-97-spice-

predicts-differential-conducted-emi-from-switching-power-supplie/ [Accessed 21 April 2022].

[17] Scottsdale Neurofeedback Institute, AZ. (n.d.). Delta Waves. [online] Available at:

http://scottsdaleneurofeedback.com/services/qeeg-brain-mapping/eeg-brainwaves/delta-

waves/ [Accessed 21 April 2022].

[18] Heckbert, P. (1995). Fourier Transforms and the Fast Fourier Transform (FFT)

Algorithm. Computer Graphics, [online] 3, pp.15–463. Available at:

https://www.cs.cmu.edu/afs/andrew/scs/cs/15-

463/2001/pub/www/notes/fourier/fourier.pdf. (https://www.cs.cmu.edu/afs/andrew/scs/cs/15-463/2001/pub/www/notes/fourier/fourier.pdf)

[19] Understanding FFTs and Windowing Overview. (n.d.). [online] Available at: https://download.ni.com/evaluation/pxi/Understanding%20FFTs%20and%20Windowing.pdf.
[20] Stanford.edu. (2011). Hamming Window. [online] Available at: https://ccrma.stanford.edu/~jos/sasp/Hamming_Window.html.
[21] Haggag, S., Mohamed, S., Bhatti, A., Haggag, H. and Nahavandi, S. (2015). Noise level classification for EEG using Hidden Markov Models. [online] IEEE Xplore. Available at: https://ieeexplore.ieee.org/document/7151974 [Accessed 22 April 2022].

[22] www.espressif.com. (n.d.). ESP32 Overview | Espressif Systems. [online] Available at:
https://www.espressif.com/en/products/socs/esp32.
[23] citeseerx.ist.psu.edu. (n.d.). Download Limit Exceeded. [online] Available at:

https://citeseerx.ist.psu.edu/viewdoc/download?doi=10.1.1.74.4153&rep=rep1&type=pdf

[Accessed 20 April 2022].

[24] Park, S. (2016). Purdue e-Pubs Measuring fluency: Temporal variables and pausing

patterns in L2 English speech. [online] Available at:

https://docs.lib.purdue.edu/cgi/viewcontent.cgi?referer=&httpsredir=1&article=1835&contex

t=open_access_dissertations. (https://docs.lib.purdue.edu/cgi/viewcontent.cgi?httpsredir=1&article=1835&context=open_access_dissertations)

[25] commons.wikimedia.org. (n.d.). Category:Sensors - Wikimedia Commons. [online]

Available at: https://commons.wikimedia.org/wiki/Category:Sensors [Accessed 18 April

2022].

[26] Johnvele (2013). audio electronics: How Negative Feedback eliminates crossover

distortion. [online] audio electronics. Available at: http://quality-audio-

electronics.blogspot.com/2013/09/how-negative-feedback-decreases.html [Accessed 19

April 2022].

[27] www.engineeringtoolbox.com. (n.d.). Required Voice Level at Distance. [online]

Available at: https://www.engineeringtoolbox.com/voice-level-d_938.html.

[28] www.wavecor.com. (n.d.). FR040WA01_02. [online] Available at:

http://www.wavecor.com/html/fr040wa01_02.html [Accessed 21 April 2022].

[29] Altium. (2021). EMI Shielding Techniques You Can Use in Your PCB Design Software. [online] Available at: https://resources.altium.com/p/emi-shielding-techniques [Accessed 30 Apr. 2022].
[30] Archambeault, B. (2008). Resistive vs. Inductive Return Current Paths. [online] Available at: https://www.emcs.org/acstrial/newsletters/fall08/tips.pdf [Accessed 27 Mar. 2022].
[31] S Vasista, S. (2017). Trace Length Calculation on PCBs. International Journal of Computer-Aided Technologies, 4(3), pp.01–08.
[32] www.sciencedirect.com. (n.d.). Wavelet Transforms - an overview | ScienceDirect

Topics. [online] Available at: https://www.sciencedirect.com/topics/computer-

science/wavelet-transforms#:~:text=The%20wavelet%20transform%20(WT)%20is [Accessed 20

April 2022].

[33] Chatterjee, S., Thakur, R.S., Yadav, R.N., Gupta, L. and Raghuvanshi, D.K. (2020). Review

of noise removal techniques in ECG signals. IET Signal Processing, 14(9), pp.569–590.

APPENDIX

- BOM for both PCB-

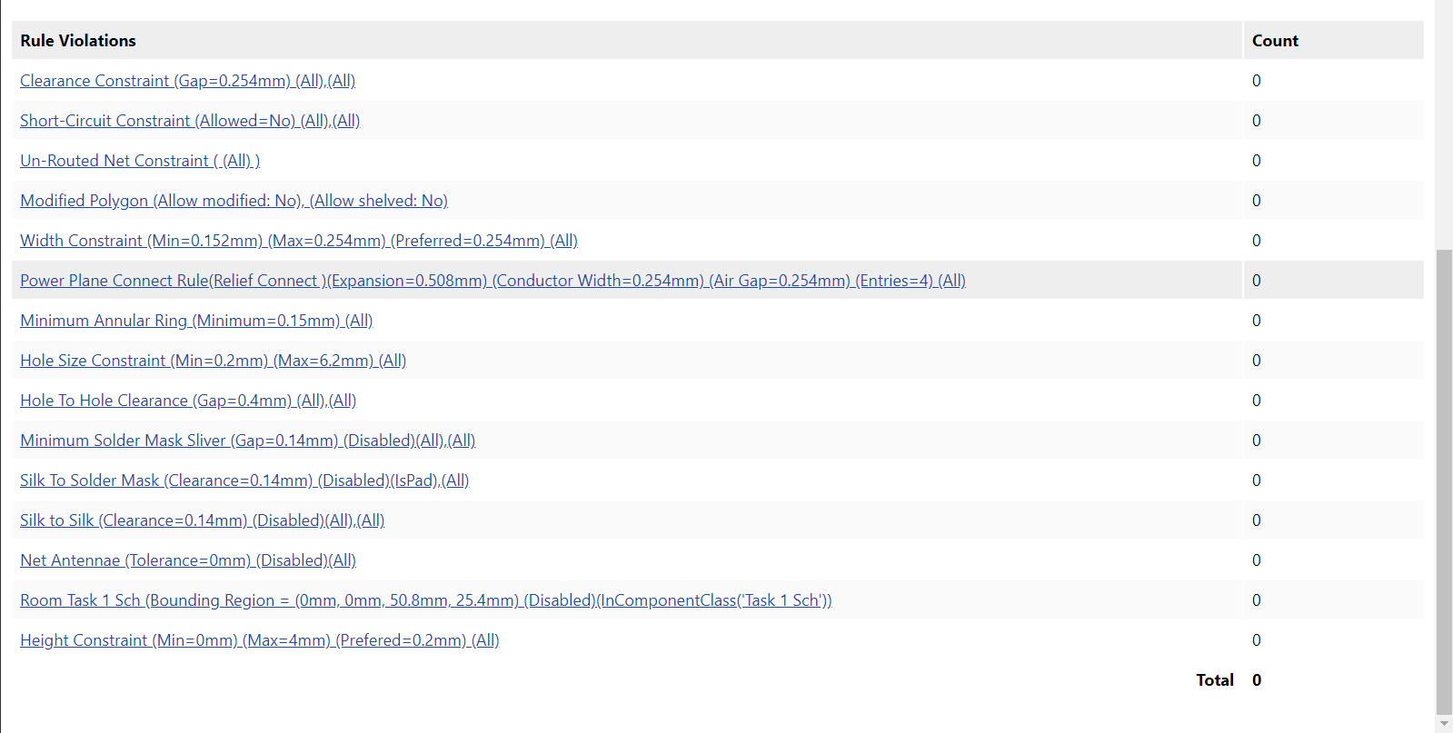
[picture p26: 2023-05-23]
DRC op sc2.PNG

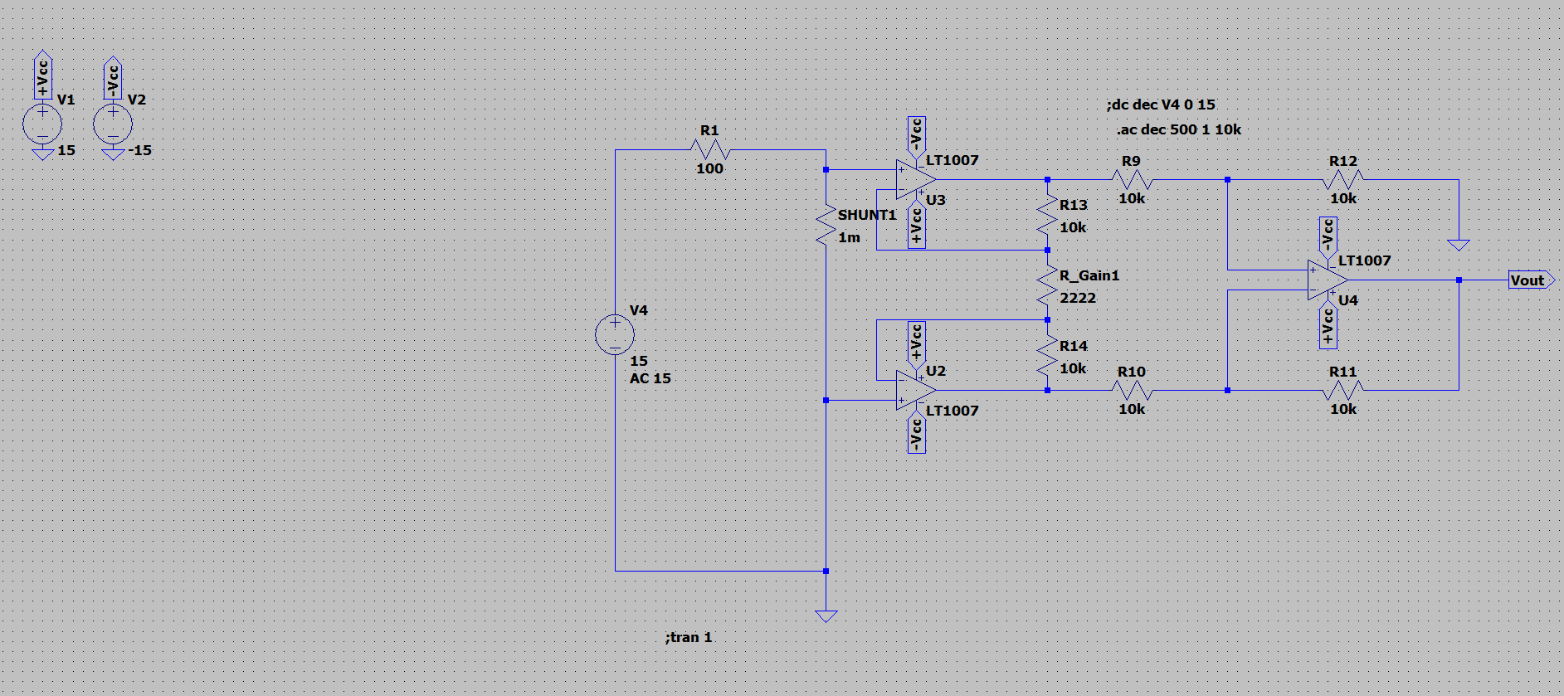
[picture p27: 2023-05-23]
sc of ckt.PNG

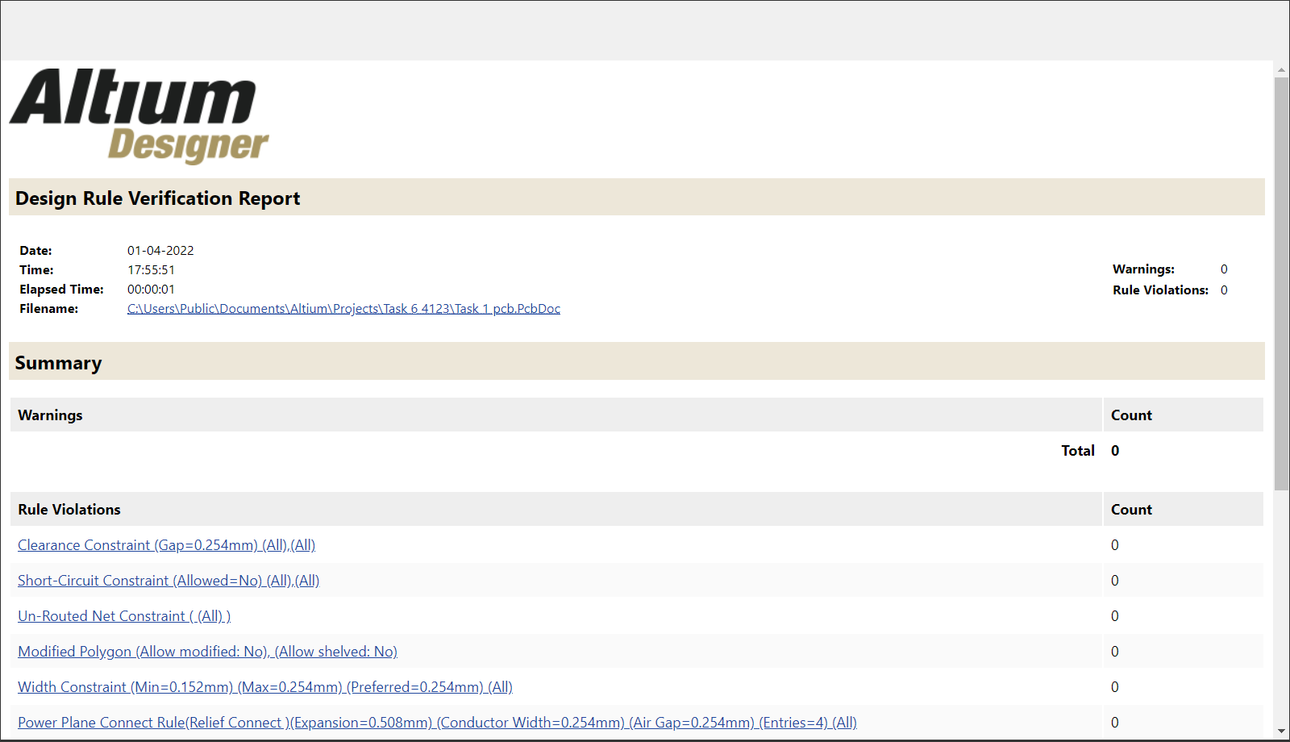
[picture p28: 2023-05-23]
DRC op sc1.PNG

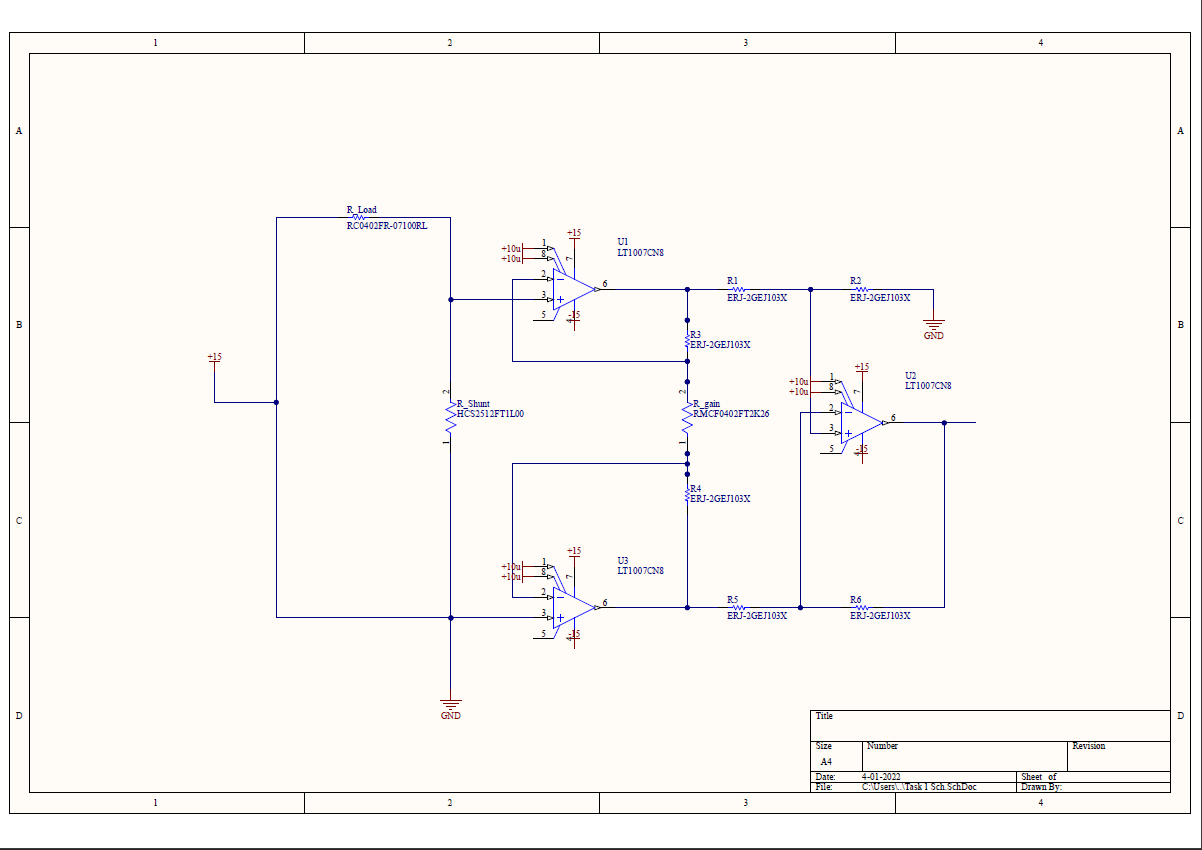
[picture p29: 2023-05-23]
sch in altium.PNG

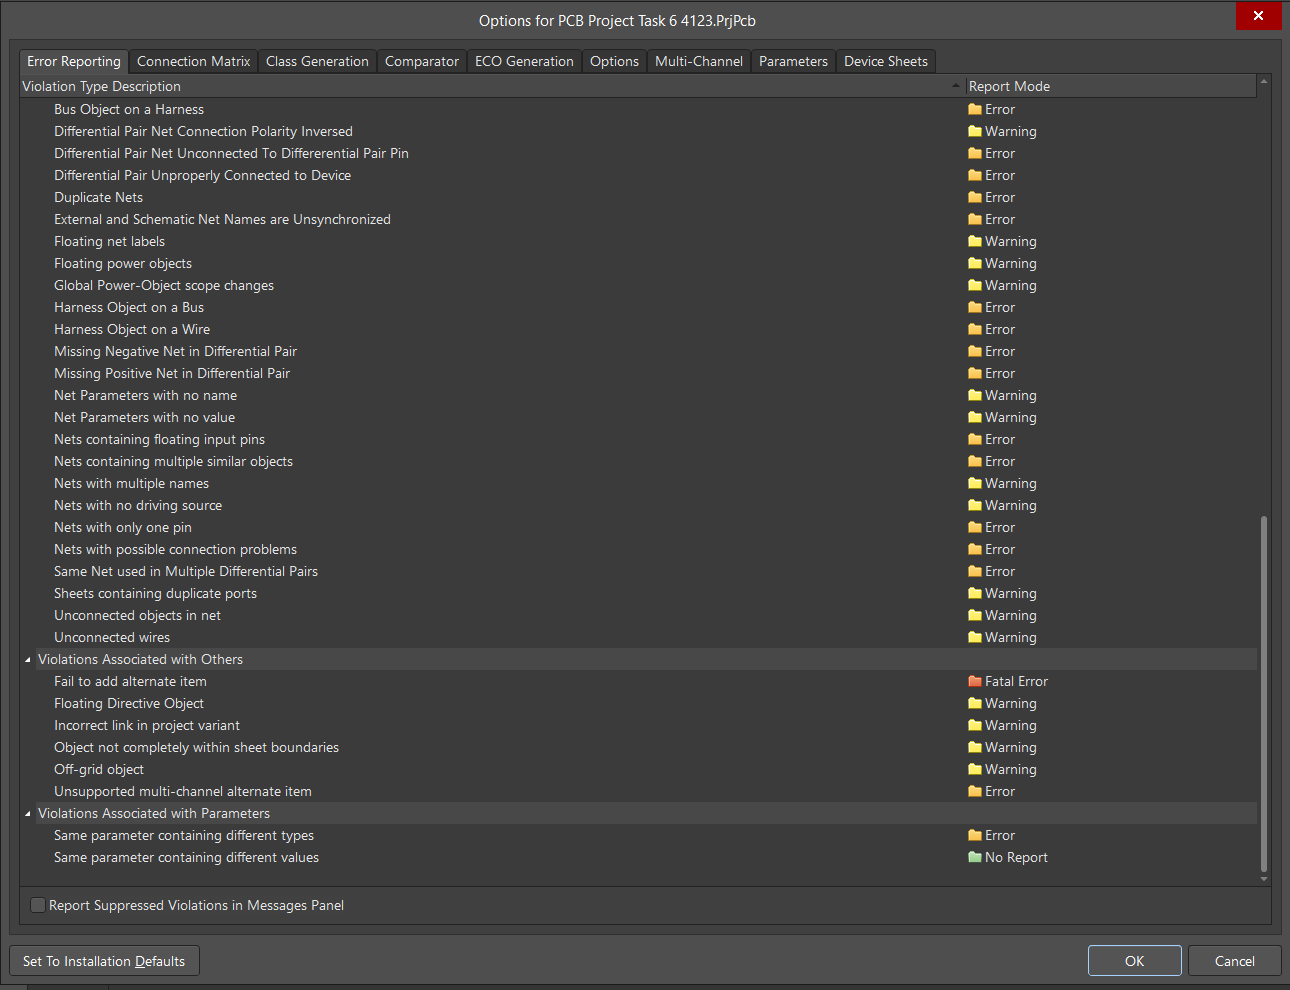
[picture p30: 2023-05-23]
ERC op log sc2.PNG

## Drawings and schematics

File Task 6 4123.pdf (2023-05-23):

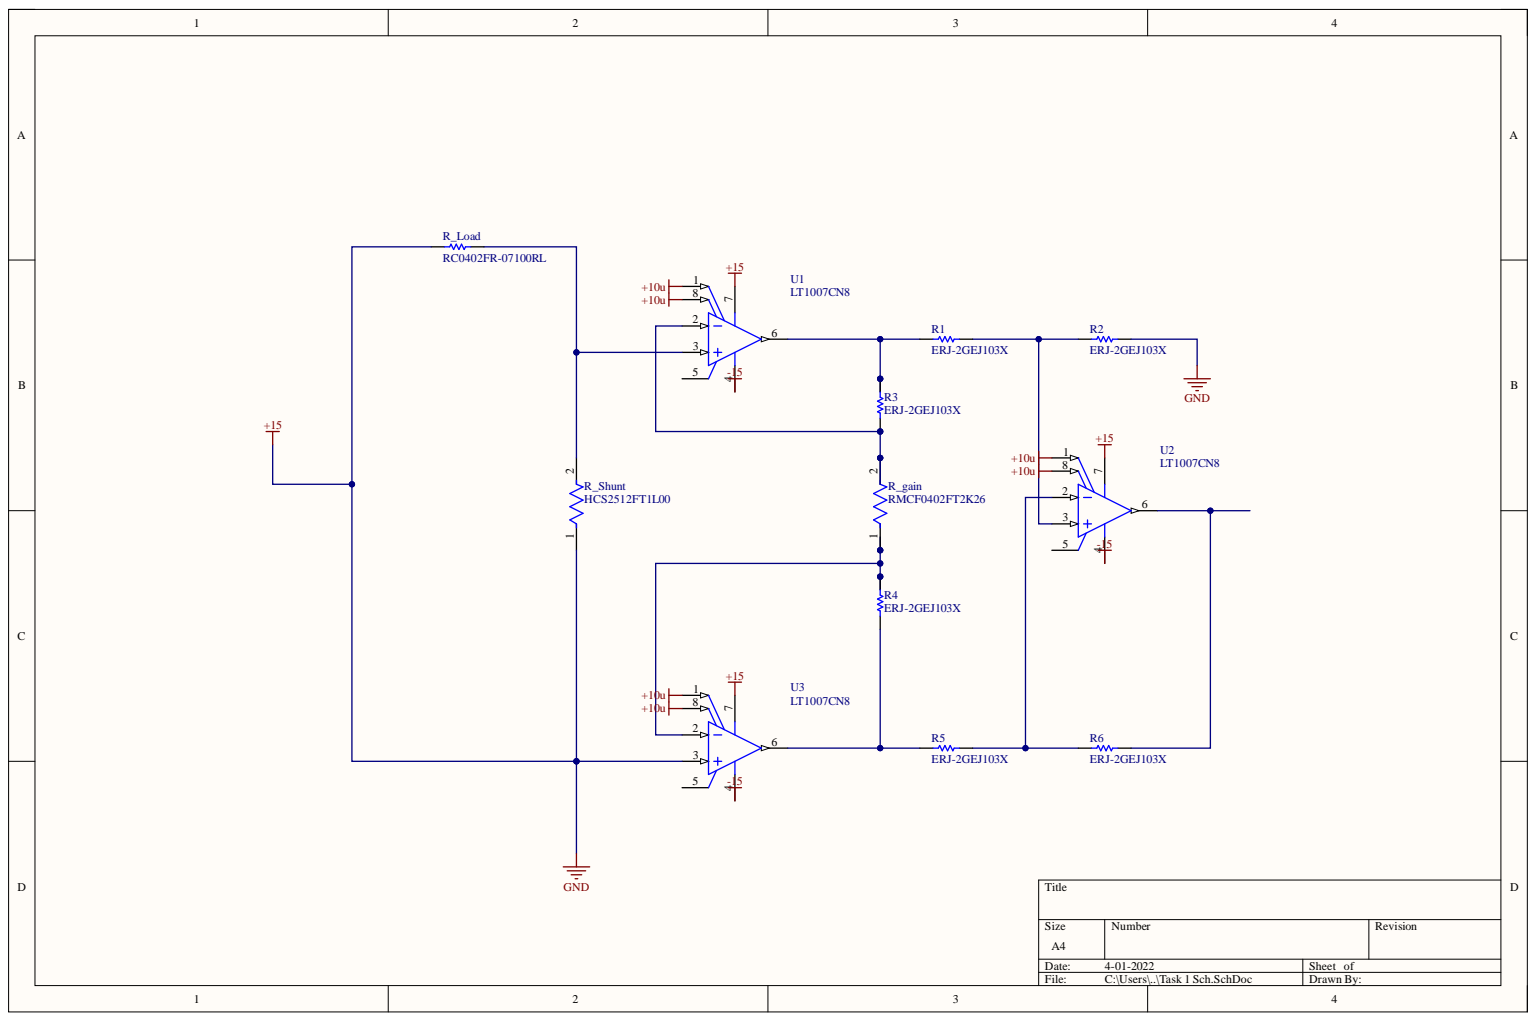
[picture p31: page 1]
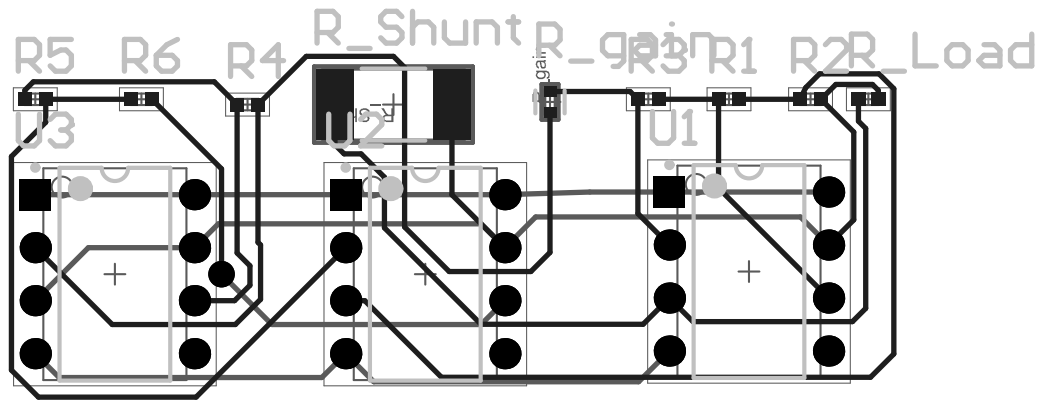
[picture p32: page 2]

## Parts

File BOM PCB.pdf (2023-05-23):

Line # | Name | Description | Designator | Revision ID | Revision State | Revision Status | Quantity | Manufacturer 1 | Manufacturer Part Number 1 | Manufacturer Lifecycle 1 | Supplier 1 | Supplier Part Number 1 | Supplier Unit Price 1 | Supplier Subtotal 1
| ERJ-2GEJ103X | | R1, R2, R3, R4, R5, R6 | | Unknown server | | 6 | Panasonic | ERJ-2GEJ103X | Volume Production | Mouser | 667-ERJ-2GEJ103X | 0.025 | 0.25
| RMCF0402FT2K26 | 2.26kΩ ±1% 0.063W 0402 Thick Film Chip Resistor AEC-Q200 compliant | R_gain | | Unknown server | | 1 | Stackpole Electronics | RMCF0402FT2K26 | Volume Production | Arrow Electronics | RMCF0402FT2K26 | 0.0231 | 0.0231
| RC0402FR-07100RL | | R_Load | | Unknown server | | 1 | Yageo | RC0402FR-07100RL | Volume Production | Newark | 45Y6897 | 0.002 | 0.002
| HCS2512FT1L00 | RES 0.001 OHM 1% 3W 2512 | R_Shunt | | Unknown server | | 1 | Stackpole Electronics | HCS2512FT1L00 | Volume Production | Arrow Electronics | HCS2512FT1L00 | 0.5086 | 0.5086
| LT1007CN8 | Single Channel, Low Noise, High Speed Precision Operational Amplifier, 8 MHz Typical GBW, 2.5 V/us Typical SR, 4 to 44 V, 8-Pin DIP (N8-8), Commerical | U1, U2, U3 | | Unknown server | | 3 | Analog Devices / Linear Technology | LT1007CN8 | Volume Production | Arrow Electronics | LT1007CN8 | 5.17 | 15.51

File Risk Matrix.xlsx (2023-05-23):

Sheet: Sheet1
 | Unmitigated Risk |  |  |  |  |  | Actions
 | ID | Risk Description | Likelihood | Impact | Severity | Owner | Mitigation Actions
Design Risks | 1 | Not completing tasks at deadlines | Possible | Moderate | Medium | Team | Drafted Gantt Chart to montior task and ensure that all team members were scheduled to complete tasks. Schedule reviews in between mentor sessions to re-align team
 | 2 | Team member overload | Possible | Significant | Medium High | Team | Ensure that mutliple people are assigned to each task. Record misunderstandings in the group document to ask each other and the mentor where applicable
 | 3 | Miscommunications | Unlikely | Moderate | Low Medium | Team | Reviews in between mentor sessions to re-align team. Use of chat to ensure all team members are able to raise and assist each other
 | 4 | Emergent Tasks | Possible | Significant | Medium High | Team | Unplanned tasks that arise shall be raised in the team chat. The team shall re-evaluate current personel distribution and re-allocate as necessary. Modifications to the team member and timeline shall be agreed by all members.
 | 5 | Losing Team Members | Very Unlikely | Severe | Medium | Team | All team members shall be familiar with the whole design. Team members shall avoid working alone and communicate often about progress.
Product Risks | 6 | SPICE Model inaccuracies | Likely | Significant | Medium High | D1, D3 | Refer to datasheets where applicable. Understand the simplifications of the SPICE model, especially active components. Perform monte-carlo and tolerance analysis.
 | 7 | Product Failure (Electrical) | Likely | Severe | High | D4 | Protetction on high current circuits. Failsafe design where potential sources of power can be eliminated safely.
 | 8 | Product Failure Performance | Unlikely | Significant | Medium | D1, D3, D4 | Key metrics shall be over designed in the models. Perform monte-carlo and tolerance analysis.
 | 9 | Product Failure Translation | Unlikely | Significant | Medium | D1, D2, D4 | Use a large sample of test cases in simulation. Ensure modelled noise is realistic. Build a metric of the translation accuracy in the test environment
 | 10 | Model Failure (Presnetation) | Very Likely | Negligible | Low Medium | Team | Before the presentation, ensure that all metrics have been documented with images in the event of a failure.

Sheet: Sheet2
Risk Matrix
 | Negligible | Minor | Moderate | Significant | Severe
Very Likely | Low Med | Medium | Med Hi | High | High
Likely | Low | Low Med | Medium | Med Hi | High
Possible | Low | Low Med | Medium | Med Hi | Med Hi
Unlikely | Low | Low Med | Low Med | Medium | Med Hi
Very Unlikely | Low | Low | Low Med | Medium | Medium
